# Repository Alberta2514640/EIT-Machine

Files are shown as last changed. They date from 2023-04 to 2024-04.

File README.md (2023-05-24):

# picoAWG
Arbitrary Waveform Generator for the Raspberry Pi Pico 16 Channels

## AWG Desktop Application
Desktop application to interface with Arbitrary Waveform Generator

TODO
- Implement Control of 16 Channels to Control Amplitude, Frequency, Offset 
- Read Back Output with Monitor to see the output
- Control LED s as needed

## PCB Design 
The board design for the waveform generator

TODO
- Update PCB design to include RP2040 directly and a cheaper OP AMP
- Update PCB design to shrink the design down to a more reasonable size and add a small status display beyond the current 5 status LEDs.

## RP2040 Code 
The code loaded onto the Pi Pico. 

TODO
- Monitor Output Needs to be fixed to setup the output
    - Write Values to the Output and Read Corresponding Voltage Changes 
- Control over channels 1-16 with Output Adjustments
    - Split the ADC control and the communication/ led control to seperate cores communicating between one another.
    - Utilize the PIO to drive the SPI peripheral and set the outputs appropriately. 
- Add functions to set the Configuration Register, Offset, Calibration, Data, Registers

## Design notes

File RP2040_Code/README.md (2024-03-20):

# RP2040 Embedded Code

This version of the RP2040 code runs on top of CircuitPython 9.0.0. It should work on earlier versions of CircuitPython as well, but they have not been tested.

CircuitPython can be downloaded [here](https://circuitpython.org/board/raspberry_pi_pico/) and the CircuitPython library bundle can be downloaded [here](https://circuitpython.org/libraries).

This project requires the `adafruit_pioasm.mpy`, `adafruit_74hc595.mpy` library files and the `adafruit_bus_directory` directory from the library bundle. Make sure you download the matching bundle for the version of CircuitPython you are using! Copy the listed items from the unzipped bundle into the `lib` directory on the RP2040's file system.

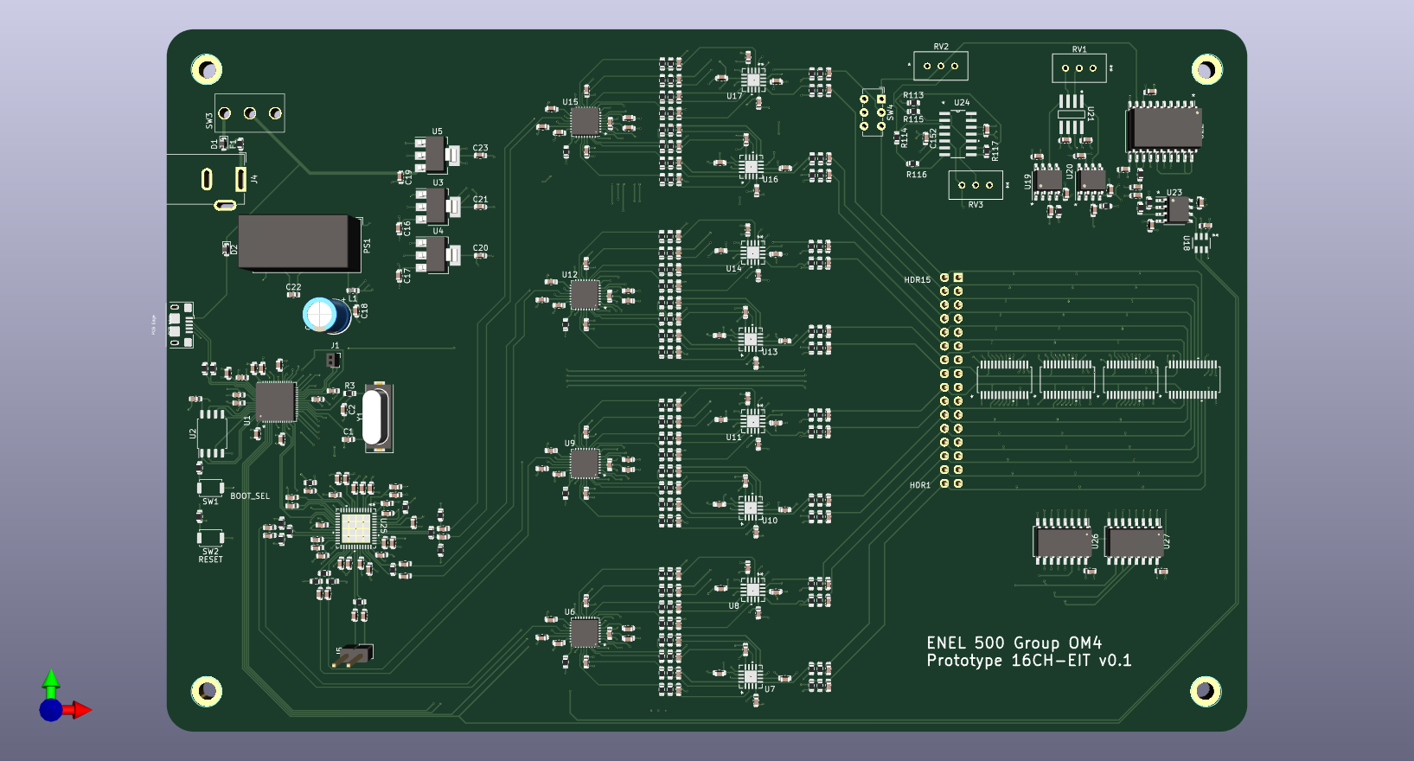
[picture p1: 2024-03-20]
PCB_Design/picoAWG_front.png

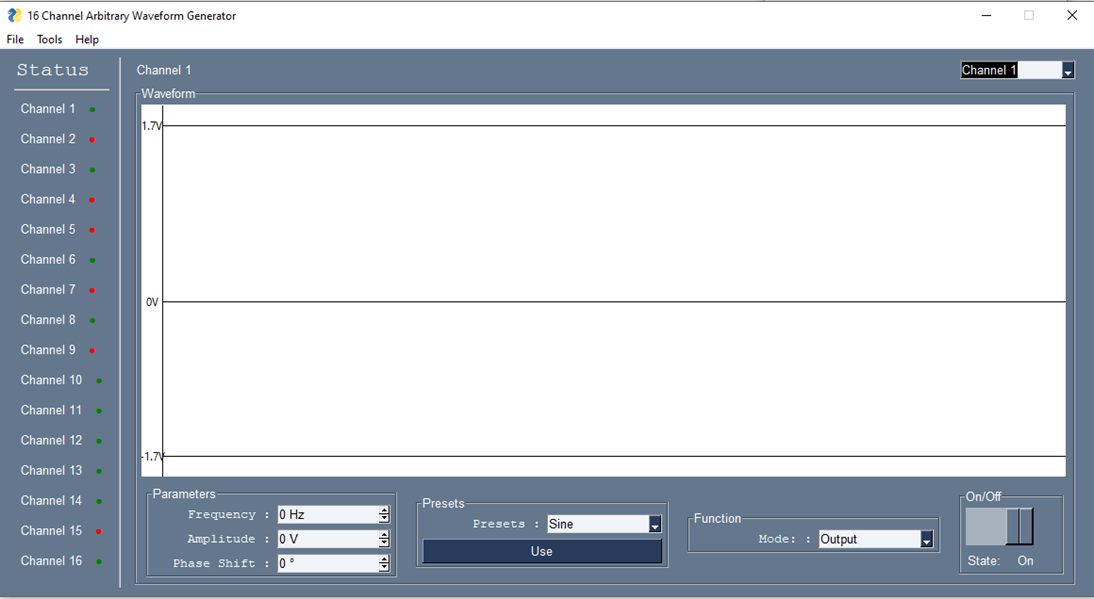
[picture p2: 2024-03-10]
AWG_DesktopApp/GUIDesign/Designed.png

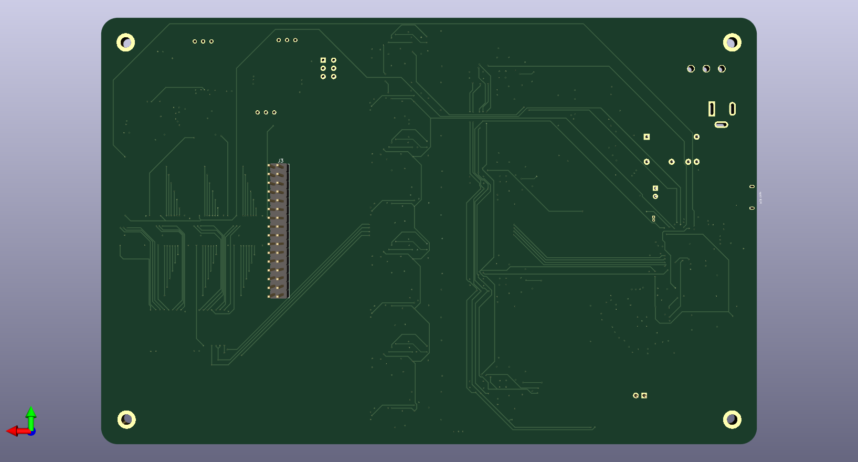
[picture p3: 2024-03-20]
PCB_Design/picoAWG_back.png

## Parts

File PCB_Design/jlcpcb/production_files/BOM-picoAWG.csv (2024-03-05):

Comment | Designator | Footprint | LCSC
SN74HC595 | U26,U27 | SOIC-16W_5.3x10.2mm_P1.27mm | C10092
27p | C1,C2 | C_0603_1608Metric | C107045
BOOT_SEL | SW1,SW2 | SW_Push_SPST_NO_Alps_SKRK | C115357
629105150521 | J2 | USB_Micro-B_Amphenol_10118193-0001LF_Horizontal | C132562
0.1u | C10,C100,C101,C102,C103,C108,C109,C11,C110,C115,C116,C117,C118,C119,C12,C124,C125,C126,C127,C128,C129,C13,C130,C131,C138,C139,C14,C140,C141,C142,C143,C144,C145,C146,C148,C149,C150,C151,C152,C153,C154,C155,C156,C157,C158,C159,C160,C161,C162,C163,C164,C165,C166,C167,C168,C169,C170,C171,C172,C173,C174,C175,C176,C177,C178,C179,C180,C181,C182,C183,C184,C185,C186,C187,C188,C189,C24,C25,C26,C3,C31,C32,C33,C34,C35,C40,C41,C42,C43,C44,C45,C46,C47,C5,C52,C53,C54,C59,C6,C60,C61,C62,C63,C68,C69,C70,C71,C72,C73,C74,C75,C8,C80,C81,C82,C87,C88,C89,C9,C90,C91,C96,C97,C98,C99 | C_0603_1608Metric | C14663
NCP1117-3.3_SOT223 | U3,U4 | SOT-223-3_TabPin2 | C146799
1u | C104,C105,C106,C107,C132,C133,C134,C135,C4,C48,C49,C50,C51,C7,C76,C77,C78,C79 | C_0603_1608Metric | C15849
1n | C136,C137 | C_0603_1608Metric | C1588
F0603E1R25FSTR | F1 | Fuse_0603_1608Metric | C163109
10p | C147 | C_0603_1608Metric | C1634
NCP1117-5.0_SOT223 | U5 | SOT-223-3_TabPin2 | C185806
10u | C16,C17,C19,C20,C21,C22,C23 | C_0603_1608Metric | C19702
RP2040 | U1 | QFN-56-1EP_7x7mm_P0.4mm_EP3.2x3.2mm | C2040
OPA4228UA | U24 | D14 | C2060814
1k | R100,R101,R113,R114,R115,R23,R24,R25,R26,R3,R4,R48,R49,R50,R51,R73,R74,R75,R76,R98,R99 | R_0603_1608Metric | C21190
470u | C15 | CP_Radial_D6.3mm_P2.50mm | C217537
100 | R123,R124,R125,R129,R131 | R_0603_1608Metric | C22775
1M | R106,R107,R109 | R_0603_1608Metric | C22935
499 | R10,R11,R116,R117,R12,R13,R14,R15,R16,R17,R18,R19,R20,R21,R31,R32,R33,R34,R35,R36,R37,R38,R39,R40,R41,R42,R43,R44,R45,R46,R56,R57,R58,R59,R6,R60,R61,R62,R63,R64,R65,R66,R67,R68,R69,R7,R70,R71,R8,R81,R82,R83,R84,R85,R86,R87,R88,R89,R9,R90,R91,R92,R93,R94,R95,R96 | R_0603_1608Metric | C23065
4.7k | R5 | R_0603_1608Metric | C23162
49.9 | R102,R103,R104,R105,R27,R28,R29,R30,R52,R53,R54,R55,R77,R78,R79,R80 | R_0603_1608Metric | C23185
240 | R119,R120,R121,R122,R126,R127 | R_0603_1608Metric | C23350
2.2u | C18 | C_0603_1608Metric | C23630
100k | R111 | R_0603_1608Metric | C25803
10k | R110 | R_0603_1608Metric | C25804
INA849DR | U21 | D0008A-IPC_A | C2871861
8.06K | R22,R47,R72,R97 | R_0603_1608Metric | C2984365
27.4 | R1,R2 | R_0603_1608Metric | C403125
1.5p | C111,C112,C113,C114,C120,C121,C122,C123,C27,C28,C29,C30,C36,C37,C38,C39,C55,C56,C57,C58,C64,C65,C66,C67,C83,C84,C85,C86,C92,C93,C94,C95 | C_0603_1608Metric | C5186670
TL071HD | U19,U20,U23 | SOIC-8_3.9x4.9mm_P1.27mm | C5214234
PMEG3020CEP | D1,D2 | D_0603_1608Metric | C552871
18u | L1 | L_0603_1608Metric | C57839
AD7680ARJZ-REEL7 | U18 | RJ_6_ADI | C578463
ADA4817-2ACPZ-R7 | U10,U11,U13,U14,U16,U17,U7,U8 | CP_16_4_ADI | C578929
ABLS-12.000MHZ-B4-T | Y1 | Crystal_SMD_HC49-SD | C596818
AD630ARZ | U22 | SOIC-20W_7.5x12.8mm_P1.27mm | C650378
AD9106BCP | U12,U15,U6,U9 | LFCSP-32-1EP_5x5mm_P0.5mm_EP3.6x3.6mm | C653186
AD9512BCPZ | U25 | CP_48_1_ADI | C653489
ADG1406BRUZ-REEL7 | U28,U29,U30,U31 | RU_28_ADI | C654796
4.12k | R128 | R_0603_1608Metric | C723644
50 | R130 | R_0603_1608Metric | C849792
W25Q128JVS | U2 | SOIC-8_5.23x5.23mm_P1.27mm | C97521

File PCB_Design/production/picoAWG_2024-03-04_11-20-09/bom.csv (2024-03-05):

Designator | Footprint | Quantity | Value | LCSC Part #
C1, C2 | 0603 | 2 | 27p
C10, C100, C101, C102, C103, C108, C109, C11, C110, C115, C116, C117, C118, C119, C12, C124, C125, C126, C127, C128, C129, C13, C130, C131, C138, C139, C14, C140, C141, C142, C143, C144, C145, C146, C148, C149, C150, C151, C152, C153, C154, C155, C156, C157, C158, C159, C160, C161, C162, C163, C164, C165, C166, C167, C168, C169, C170, C171, C172, C173, C174, C175, C176, C177, C178, C179, C180, C181, C182, C183, C184, C185, C186, C187, C188, C189, C24, C25, C26, C3, C31, C32, C33, C34, C35, C40, C41, C42, C43, C44, C45, C46, C47, C5, C52, C53, C54, C59, C6, C60, C61, C62, C63, C68, C69, C70, C71, C72, C73, C74, C75, C8, C80, C81, C82, C87, C88, C89, C9, C90, C91, C96, C97, C98, C99 | 0603 | 125 | 0.1u
C104, C105, C106, C107, C132, C133, C134, C135, C4, C48, C49, C50, C51, C7, C76, C77, C78, C79 | 0603 | 18 | 1u
C111, C112, C113, C114, C120, C121, C122, C123, C27, C28, C29, C30, C36, C37, C38, C39, C55, C56, C57, C58, C64, C65, C66, C67, C83, C84, C85, C86, C92, C93, C94, C95 | 0603 | 32 | 1.5p
C136, C137 | 0603 | 2 | 1n
C147 | 0603 | 1 | 10p
C15 | 0603 | 1 | 470u
C16, C17, C19, C20, C21, C22, C23 | 0603 | 7 | 10u
C18 | 0603 | 1 | 2.2u
D1, D2 | 0603 | 2 | PMEG3020CEP
F1 | 0603 | 1 | F0603E1R25FSTR
J1 | PinSocket_1x02_P1.00mm_Vertical | 1 | SWD_JP
J2 | USB_Micro-B_Wuerth_629105150521 | 1 | 629105150521
J3 | PinHeader_2x16_P2.54mm_Vertical | 1 | Conn_02x16
J4 | BarrelJack_GCT_DCJ200-10-A_Horizontal | 1 | Barrel_Jack
J5 | PinHeader_1x02_P2.54mm_Vertical | 1 | CLK4_DIAG
L1 | 0603 | 1 | 18u
PS1 | Converter_DCDC_XP_POWER-IAxxxxD_THT | 1 | IA0515D
R1, R2 | 0603 | 2 | 27.4
R10, R11, R12, R13, R14, R15, R16, R17, R18, R19, R20, R21, R31, R32, R33, R34, R35, R36, R37, R38, R39, R40, R41, R42, R43, R44, R45, R46, R56, R57, R58, R59, R6, R60, R61, R62, R63, R64, R65, R66, R67, R68, R69, R7, R70, R71, R8, R81, R82, R83, R84, R85, R86, R87, R88, R89, R9, R90, R91, R92, R93, R94, R95, R96 | 0603 | 64 | 499
R100, R101, R113, R114, R115, R23, R24, R25, R26, R3, R4, R48, R49, R50, R51, R73, R74, R75, R76, R98, R99 | 0603 | 21 | 1k
R102, R103, R104, R105, R27, R28, R29, R30, R52, R53, R54, R55, R77, R78, R79, R80 | 0603 | 16 | 49.9
R106, R107, R109 | 0603 | 3 | 1M
R110 | 0603 | 1 | 10k
R111 | 0603 | 1 | 100k
R116, R117 | 0603 | 2 | 500
R119, R120, R121, R122, R126, R127 | 0603 | 6 | 240
R123, R124, R125, R129, R131 | 0603 | 5 | 100
R128 | 0603 | 1 | 4.12k
R130 | 0603 | 1 | 50
R22, R47, R72, R97 | 0603 | 4 | 8.06K
R5 | 0603 | 1 | 4.7k
RV1, RV2 | POT_2023-08-01_VIS | 2 | M64W202KB40
RV3 | POT_2023-08-01_VIS | 1 | M64W103KB40
SW1 | SW_Push_SPST_NO_Alps_SKRK | 1 | BOOT_SEL
SW2 | SW_Push_SPST_NO_Alps_SKRK | 1 | SW_Push
SW3 | ANT11SF1CQE | 1 | ANT11SF1CQE
SW4 | SW_E-Switch_EG1271_SPDT | 1 | SW_SPDT_321
U1 | QFN-56-1EP_7x7mm_P0.4mm_EP3.2x3.2mm | 1 | RP2040
U10, U11, U13, U14, U16, U17, U7, U8 | CP_16_4_ADI | 8 | ADA4817-2ACPZ-R7
U12, U15, U6, U9 | LFCSP-32-1EP_5x5mm_P0.5mm_EP3.6x3.6mm | 4 | AD9106BCP
U18 | RJ_6_ADI | 1 | AD7680ARJZ-REEL7
U19, U20, U23 | TSSOP-8_3x3mm_P0.65mm | 3 | TL071
U2 | SOIC-8_5.23x5.23mm_P1.27mm | 1 | W25Q128JVS
U21 | D0008A-IPC_A | 1 | INA849DR
U22 | SOIC-20W_7.5x12.8mm_P1.27mm | 1 | AD630ARZ
U24 | D14 | 1 | OPA4228UA
U25 | CP_48_1_ADI | 1 | AD9512BCPZ
U26, U27 | SOIC-16W_5.3x10.2mm_P1.27mm | 2 | SN74HC595
U28, U29, U30, U31 | RU_28_ADI | 4 | ADG1406BRUZ-REEL7
U3, U4 | SOT-223-3_TabPin2 | 2 | NCP1117-3.3_SOT223
U5 | SOT-223-3_TabPin2 | 1 | NCP1117-5.0_SOT223
Y1 | Crystal_SMD_HC49-SD | 1 | ABLS-12.000MHZ-B4-T

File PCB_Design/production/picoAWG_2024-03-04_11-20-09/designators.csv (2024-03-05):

C1:1
C10:1
C100:1
C101:1
C102:1
C103:1
C104:1
C105:1
C106:1
C107:1
C108:1
C109:1
C11:1
C110:1
C111:1
C112:1
C113:1
C114:1
C115:1
C116:1
C117:1
C118:1
C119:1
C12:1
C120:1
C121:1
C122:1
C123:1
C124:1
C125:1
C126:1
C127:1
C128:1
C129:1
C13:1
C130:1
C131:1
C132:1
C133:1
C134:1
C135:1
C136:1
C137:1
C138:1
C139:1
C14:1
C140:1
C141:1
C142:1
C143:1
C144:1
C145:1
C146:1
C147:1
C148:1
C149:1
C15:1
C150:1
C151:1
C152:1
C153:1
C154:1
C155:1
C156:1
C157:1
C158:1
C159:1
C16:1
C160:1
C161:1
C162:1
C163:1
C164:1
C165:1
C166:1
C167:1
C168:1
C169:1
C17:1
C170:1
C171:1
C172:1
C173:1
C174:1
C175:1
C176:1
C177:1
C178:1
C179:1
C18:1
C180:1
C181:1
C182:1
C183:1
C184:1
C185:1
C186:1
C187:1
C188:1
C189:1
C19:1
C2:1
C20:1
C21:1
C22:1
C23:1
C24:1
C25:1
C26:1
C27:1
C28:1
C29:1
C3:1
C30:1
C31:1
C32:1
C33:1
C34:1
C35:1
C36:1
C37:1
C38:1
C39:1
C4:1
C40:1
C41:1
C42:1
C43:1
C44:1
C45:1
C46:1
C47:1
C48:1
C49:1
C5:1
C50:1
C51:1
C52:1
C53:1
C54:1
C55:1
C56:1
C57:1
C58:1
C59:1
C6:1
C60:1
C61:1
C62:1
C63:1
C64:1
C65:1
C66:1
C67:1
C68:1
C69:1
C7:1
C70:1
C71:1
C72:1
C73:1
C74:1
C75:1
C76:1
C77:1
C78:1
C79:1
C8:1
C80:1
C81:1
C82:1
C83:1
C84:1
C85:1
C86:1
C87:1
C88:1
C89:1
C9:1
C90:1
C91:1
C92:1
C93:1
C94:1
C95:1
C96:1
C97:1
C98:1
C99:1
D1:1
D2:1
F1:1
J1:1
J2:1
J3:1
J4:1
J5:1
L1:1
PS1:1
R1:1
R10:1
R100:1
R101:1
R102:1
R103:1
R104:1
R105:1
R106:1
R107:1
R109:1
R11:1
R110:1
R111:1
R113:1
R114:1
R115:1
R116:1
R117:1
R119:1
R12:1
R120:1
R121:1
R122:1
R123:1
R124:1
R125:1
R126:1
R127:1
R128:1
R129:1
R13:1
R130:1
R131:1
R14:1
R15:1
R16:1
R17:1
R18:1
R19:1
R2:1
R20:1
R21:1
R22:1
R23:1
R24:1
R25:1
R26:1
R27:1
R28:1
R29:1
R3:1
R30:1
R31:1
R32:1
R33:1
R34:1
R35:1
R36:1
R37:1
R38:1
R39:1
R4:1
R40:1
R41:1
R42:1
R43:1
R44:1
R45:1
R46:1
R47:1
R48:1
R49:1
R5:1
R50:1
R51:1
R52:1
R53:1
R54:1
R55:1
R56:1
R57:1
R58:1
R59:1
R6:1
R60:1
R61:1
R62:1
R63:1
R64:1
R65:1
R66:1
R67:1
R68:1
R69:1
R7:1
R70:1
R71:1
R72:1
R73:1
R74:1
R75:1
R76:1
R77:1
R78:1
R79:1
R8:1
R80:1
R81:1
R82:1
R83:1
R84:1
R85:1
R86:1
R87:1
R88:1
R89:1
R9:1
R90:1
R91:1
R92:1
R93:1
R94:1
R95:1
R96:1
R97:1
R98:1
R99:1
REF**:4
RV1:1
RV2:1
RV3:1
SW1:1
SW2:1
SW3:1
SW4:1
U1:1
U10:1
U11:1
U12:1
U13:1
U14:1
U15:1
U16:1
U17:1
U18:1
U19:1
U2:1
U20:1
U21:1
U22:1
U23:1
U24:1
U25:1
U26:1
U27:1
U28:1
U29:1
U3:1
U30:1
U31:1
U4:1
U5:1
U6:1
U7:1
U8:1
U9:1
Y1:1

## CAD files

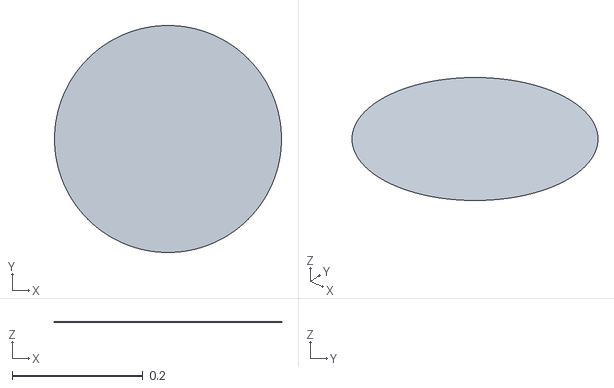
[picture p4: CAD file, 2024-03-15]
AWG_DesktopApp/EIT/JAC/Meshes/Circle.ply
0.348 x 0.348 x 3.04e-08

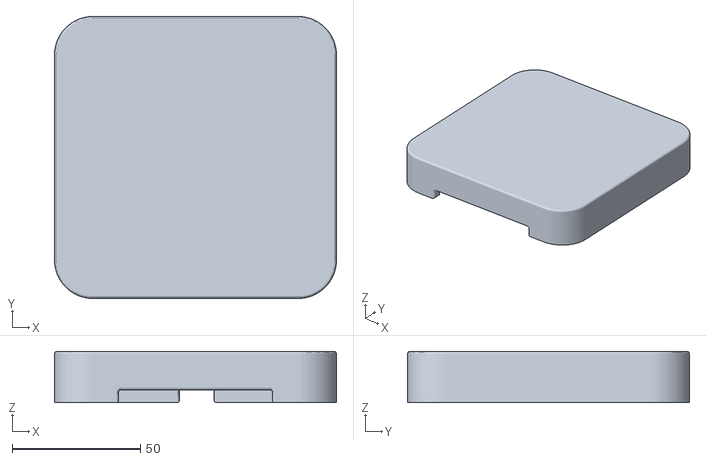
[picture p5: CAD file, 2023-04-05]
Enclosure/AWG v1_Top.stl
110.0 x 110.0 x 20.0

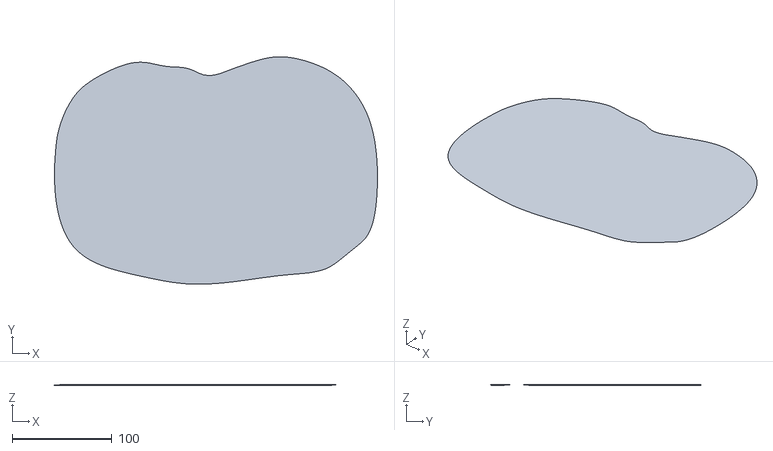
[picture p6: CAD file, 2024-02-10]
AWG_DesktopApp/EIT/JAC/Meshes/mesha06_bumpychestslice_radiological_view_both_lungs_1_0-3.ply
324.5 x 228.5 x 2e-05

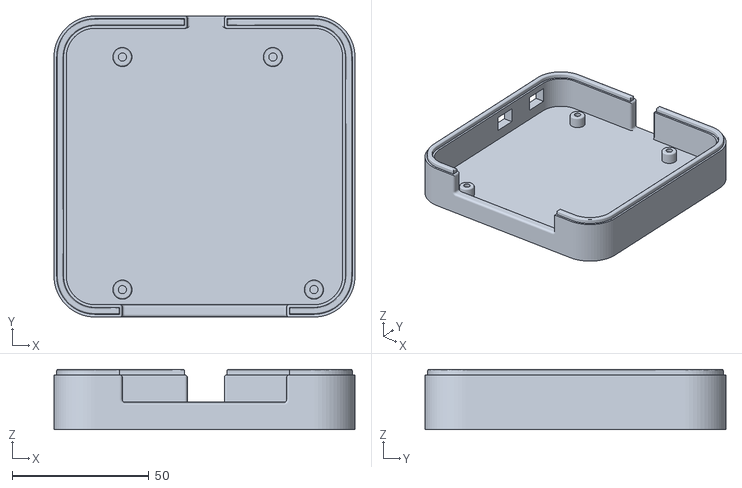
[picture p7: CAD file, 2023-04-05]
Enclosure/AWG v1_Bottom.stl
110.0 x 110.0 x 22.0

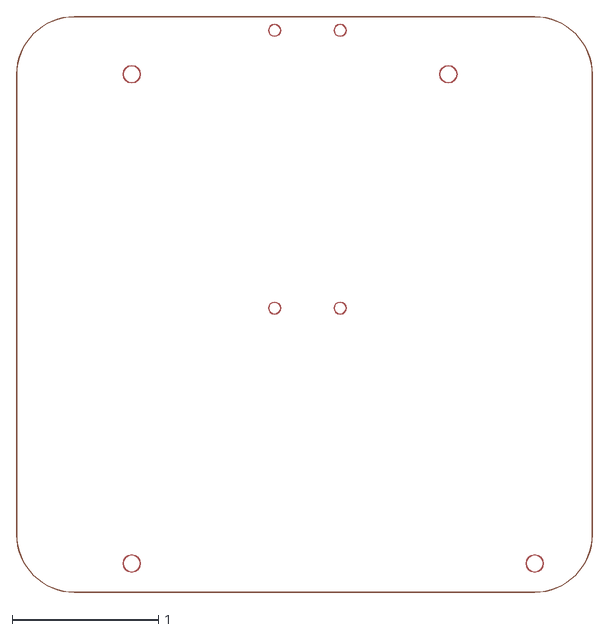
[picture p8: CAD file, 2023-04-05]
Enclosure/BoardOutline.dxf
3.94 x 3.94

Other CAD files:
Enclosure/AWG v1.f3d

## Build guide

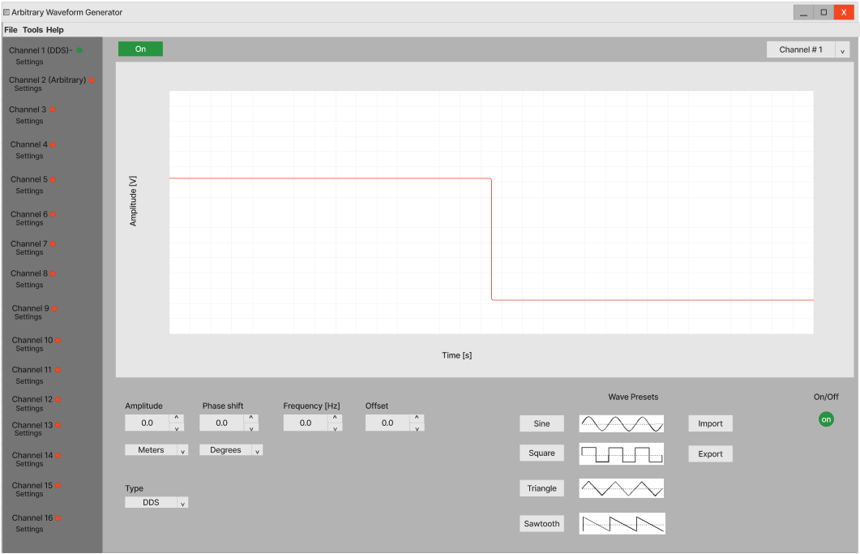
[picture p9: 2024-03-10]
AWG_DesktopApp/GUIDesign/Figma.png

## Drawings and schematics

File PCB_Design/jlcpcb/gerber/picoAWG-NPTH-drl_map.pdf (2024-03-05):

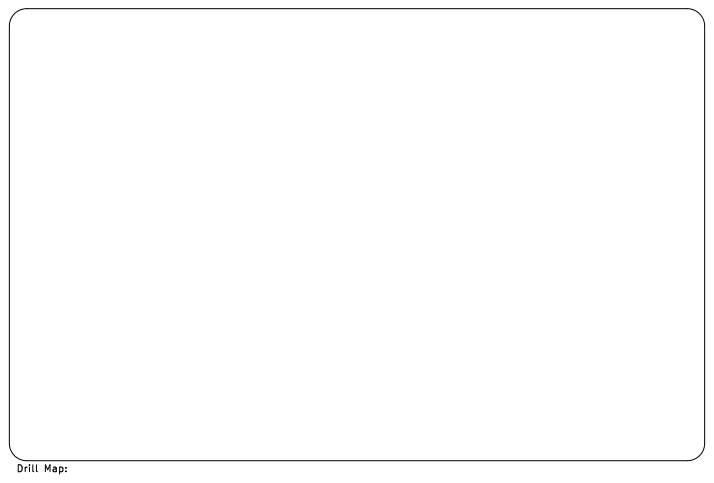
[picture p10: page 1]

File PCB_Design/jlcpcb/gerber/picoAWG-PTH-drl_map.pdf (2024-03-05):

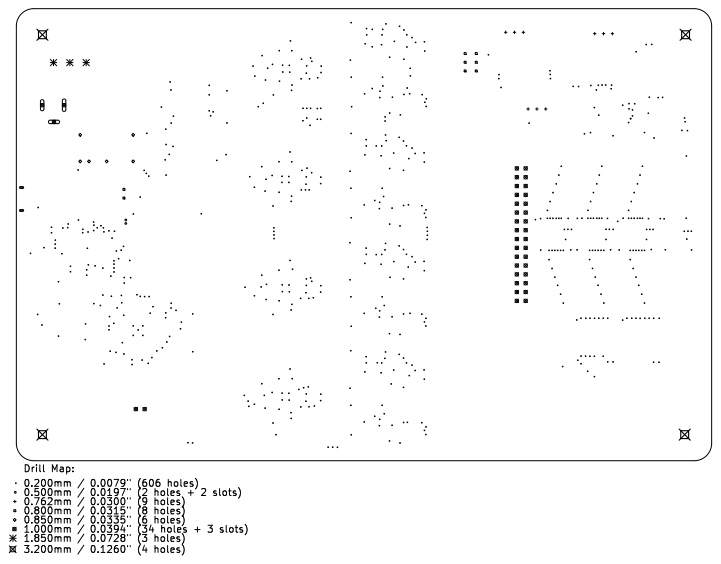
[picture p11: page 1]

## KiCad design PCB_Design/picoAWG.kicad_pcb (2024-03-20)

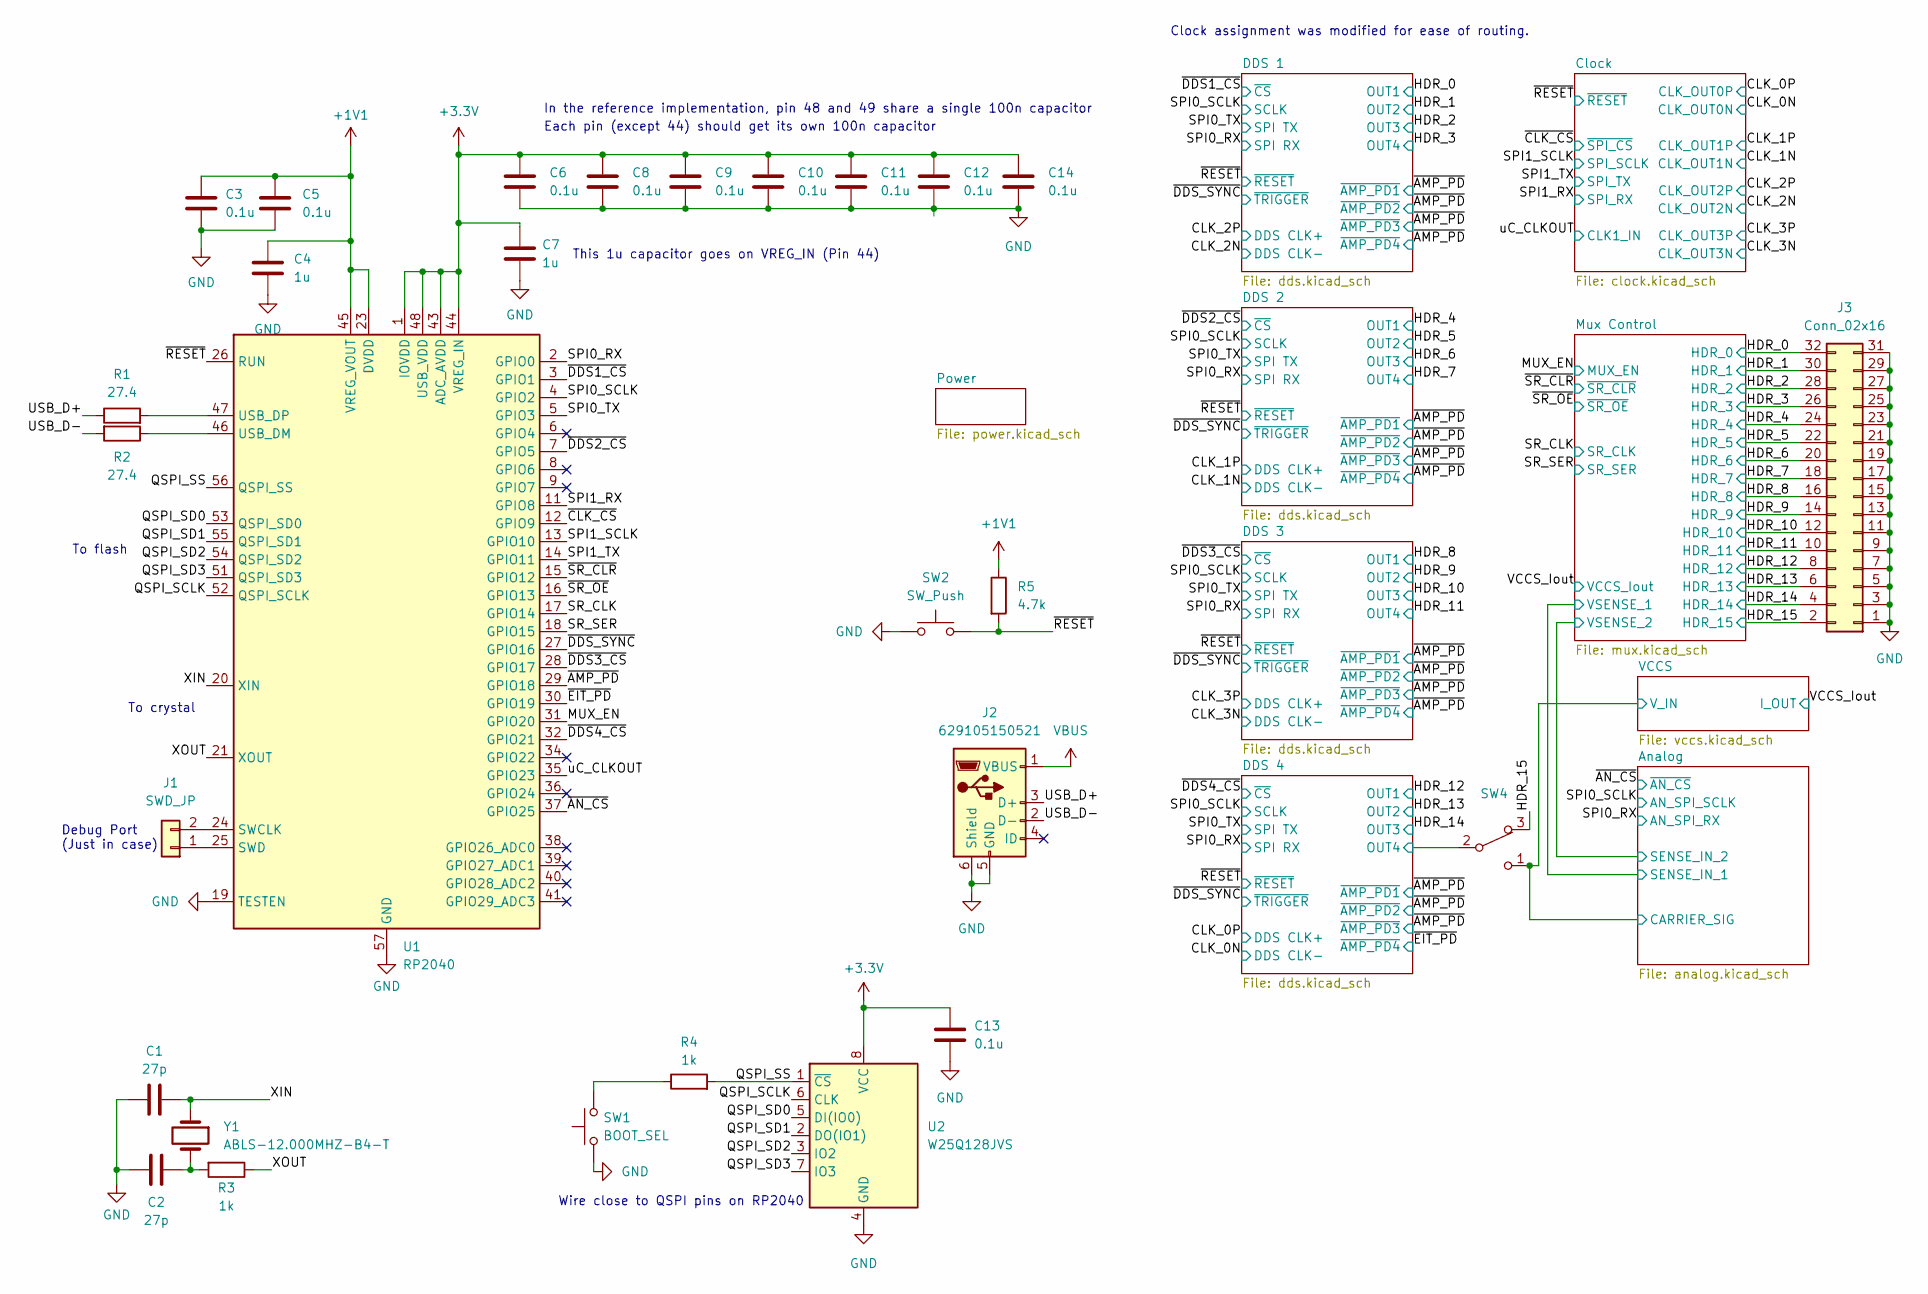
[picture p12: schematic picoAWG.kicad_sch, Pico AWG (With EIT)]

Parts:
C1, C2: 27p; C_0603_1608Metric
C3, C5, C6, C8, C9, C10, C11, C12, C13, C14: 0.1u; C_0603_1608Metric
C4, C7: 1u; C_0603_1608Metric
J1: SWD_JP; PinSocket_1x02_P1.00mm_Vertical
J2: 629105150521; USB_Micro-B_Amphenol_10118193-0001LF_Horizontal
J3: Conn_02x16; PinHeader_2x16_P2.54mm_Vertical
R1, R2: 27.4; R_0603_1608Metric
R3, R4: 1k; R_0603_1608Metric
R5: 4.7k; R_0603_1608Metric
SW1: BOOT_SEL; SW_Push_SPST_NO_Alps_SKRK
SW2: SW_Push; SW_Push_SPST_NO_Alps_SKRK
SW4: SW_SPDT_321; SW_E-Switch_EG1271_SPDT
U1: RP2040; QFN-56-1EP_7x7mm_P0.4mm_EP3.2x3.2mm
U2: W25Q128JVS; SOIC-8_5.23x5.23mm_P1.27mm
Y1: ABLS-12.000MHZ-B4-T; Crystal_SMD_HC49-SD

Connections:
+1V1: C3.1, C4.1, C5.1, R5.1, U1.23 (DVDD), U1.45 (VREG_VOUT), U1.50 (DVDD)
+3.3V: C6.1, C7.1, C8.1, C9.1, C10.1, C11.1, C12.1, C13.1, C14.1, U1.1 (IOVDD), U1.10 (IOVDD), U1.22 (IOVDD), U1.33 (IOVDD), U1.42 (IOVDD), U1.43 (ADC_AVDD), U1.44 (VREG_IN), U1.48 (USB_VDD), U1.49 (IOVDD), U2.8 (VCC); also elsewhere on the board
/Analog/CARRIER_SIG: SW4.1 (C); also elsewhere on the board
/DDS 4/OUT4: SW4.2 (B); also elsewhere on the board
/HDR_0: J3.32; also elsewhere on the board
/HDR_1: J3.30; also elsewhere on the board
/HDR_2: J3.28; also elsewhere on the board
/HDR_3: J3.26; also elsewhere on the board
/HDR_4: J3.24; also elsewhere on the board
/HDR_5: J3.22; also elsewhere on the board
/HDR_6: J3.20; also elsewhere on the board
/HDR_7: J3.18; also elsewhere on the board
/HDR_8: J3.16; also elsewhere on the board
/HDR_9: J3.14; also elsewhere on the board
/HDR_10: J3.12; also elsewhere on the board
/HDR_11: J3.10; also elsewhere on the board
/HDR_12: J3.8; also elsewhere on the board
/HDR_13: J3.6; also elsewhere on the board
/HDR_14: J3.4; also elsewhere on the board
/HDR_15: J3.2, SW4.3 (A); also elsewhere on the board
/MUX_EN: U1.31 (GPIO20); also elsewhere on the board
/QSPI_SCLK: U1.52 (QSPI_SCLK), U2.6 (CLK)
/QSPI_SD0: U1.53 (QSPI_SD0), U2.5 (DI(IO0))
/QSPI_SD1: U1.55 (QSPI_SD1), U2.2 (DO(IO1))
/QSPI_SD2: U1.54 (QSPI_SD2), U2.3 (IO2)
/QSPI_SD3: U1.51 (QSPI_SD3), U2.7 (IO3)
/QSPI_SS: R4.2, U1.56 (QSPI_SS), U2.1 (~CS)
/SPI0_RX: U1.2 (GPIO0); also elsewhere on the board
/SPI0_SCLK: U1.4 (GPIO2); also elsewhere on the board
/SPI0_TX: U1.5 (GPIO3); also elsewhere on the board
/SPI1_RX: U1.11 (GPIO8); also elsewhere on the board
/SPI1_SCLK: U1.13 (GPIO10); also elsewhere on the board
/SPI1_TX: U1.14 (GPIO11); also elsewhere on the board
/SR_CLK: U1.17 (GPIO14); also elsewhere on the board
/SR_SER: U1.18 (GPIO15); also elsewhere on the board
/USB_D+: J2.3 (D+), R1.1
/USB_D-: J2.2 (D-), R2.2
/XIN: C1.2, U1.20 (XIN), Y1.1
/XOUT: R3.1, U1.21 (XOUT)
/uC_CLKOUT: U1.35 (GPIO23); also elsewhere on the board
/~AMP_PD: U1.29 (GPIO18); also elsewhere on the board
/~AN_CS: U1.37 (GPIO25); also elsewhere on the board
/~CLK_CS: U1.12 (GPIO9); also elsewhere on the board
/~DDS1_CS: U1.3 (GPIO1); also elsewhere on the board
/~DDS2_CS: U1.7 (GPIO5); also elsewhere on the board
/~DDS3_CS: U1.28 (GPIO17); also elsewhere on the board
/~DDS4_CS: U1.32 (GPIO21); also elsewhere on the board
/~DDS_SYNC: U1.27 (GPIO16); also elsewhere on the board
/~EIT_PD: U1.30 (GPIO19); also elsewhere on the board
/~RESET: R5.2, SW2.2, U1.26 (RUN); also elsewhere on the board
/~SR_CLR: U1.15 (GPIO12); also elsewhere on the board
/~SR_OE: U1.16 (GPIO13); also elsewhere on the board
GND: C1.1, C2.2, C3.2, C4.2, C5.2, C6.2, C7.2, C8.2, C9.2, C10.2, C11.2, C12.2, C13.2, C14.2, J2.5 (GND), J2.6 (Shield), J3.1, J3.3, J3.5, J3.7, J3.9, J3.11, J3.13, J3.15, J3.17, J3.19, J3.21, J3.23, J3.25, J3.27, J3.29, J3.31, SW1.1, SW2.1, U1.19 (TESTEN), U1.57 (GND), U2.4 (GND); also elsewhere on the board
unnamed: C2.1, R3.2, Y1.2
unnamed: J1.1, U1.25 (SWD)
unnamed: J1.2, U1.24 (SWCLK)
unnamed: R4.1, SW1.2
unnamed: R2.1, U1.46 (USB_DM)
unnamed: R1.2, U1.47 (USB_DP)
VBUS: J2.1 (VBUS); also elsewhere on the board

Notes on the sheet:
Each pin (except 44) should get its own 100n capacitor
To crystal
Debug Port (Just in case)
This 1u capacitor goes on VREG_IN (Pin 44)
To flash
Clock assignment was modified for ease of routing.
In the reference implementation, pin 48 and 49 share a single 100n capacitor
Wire close to QSPI pins on RP2040

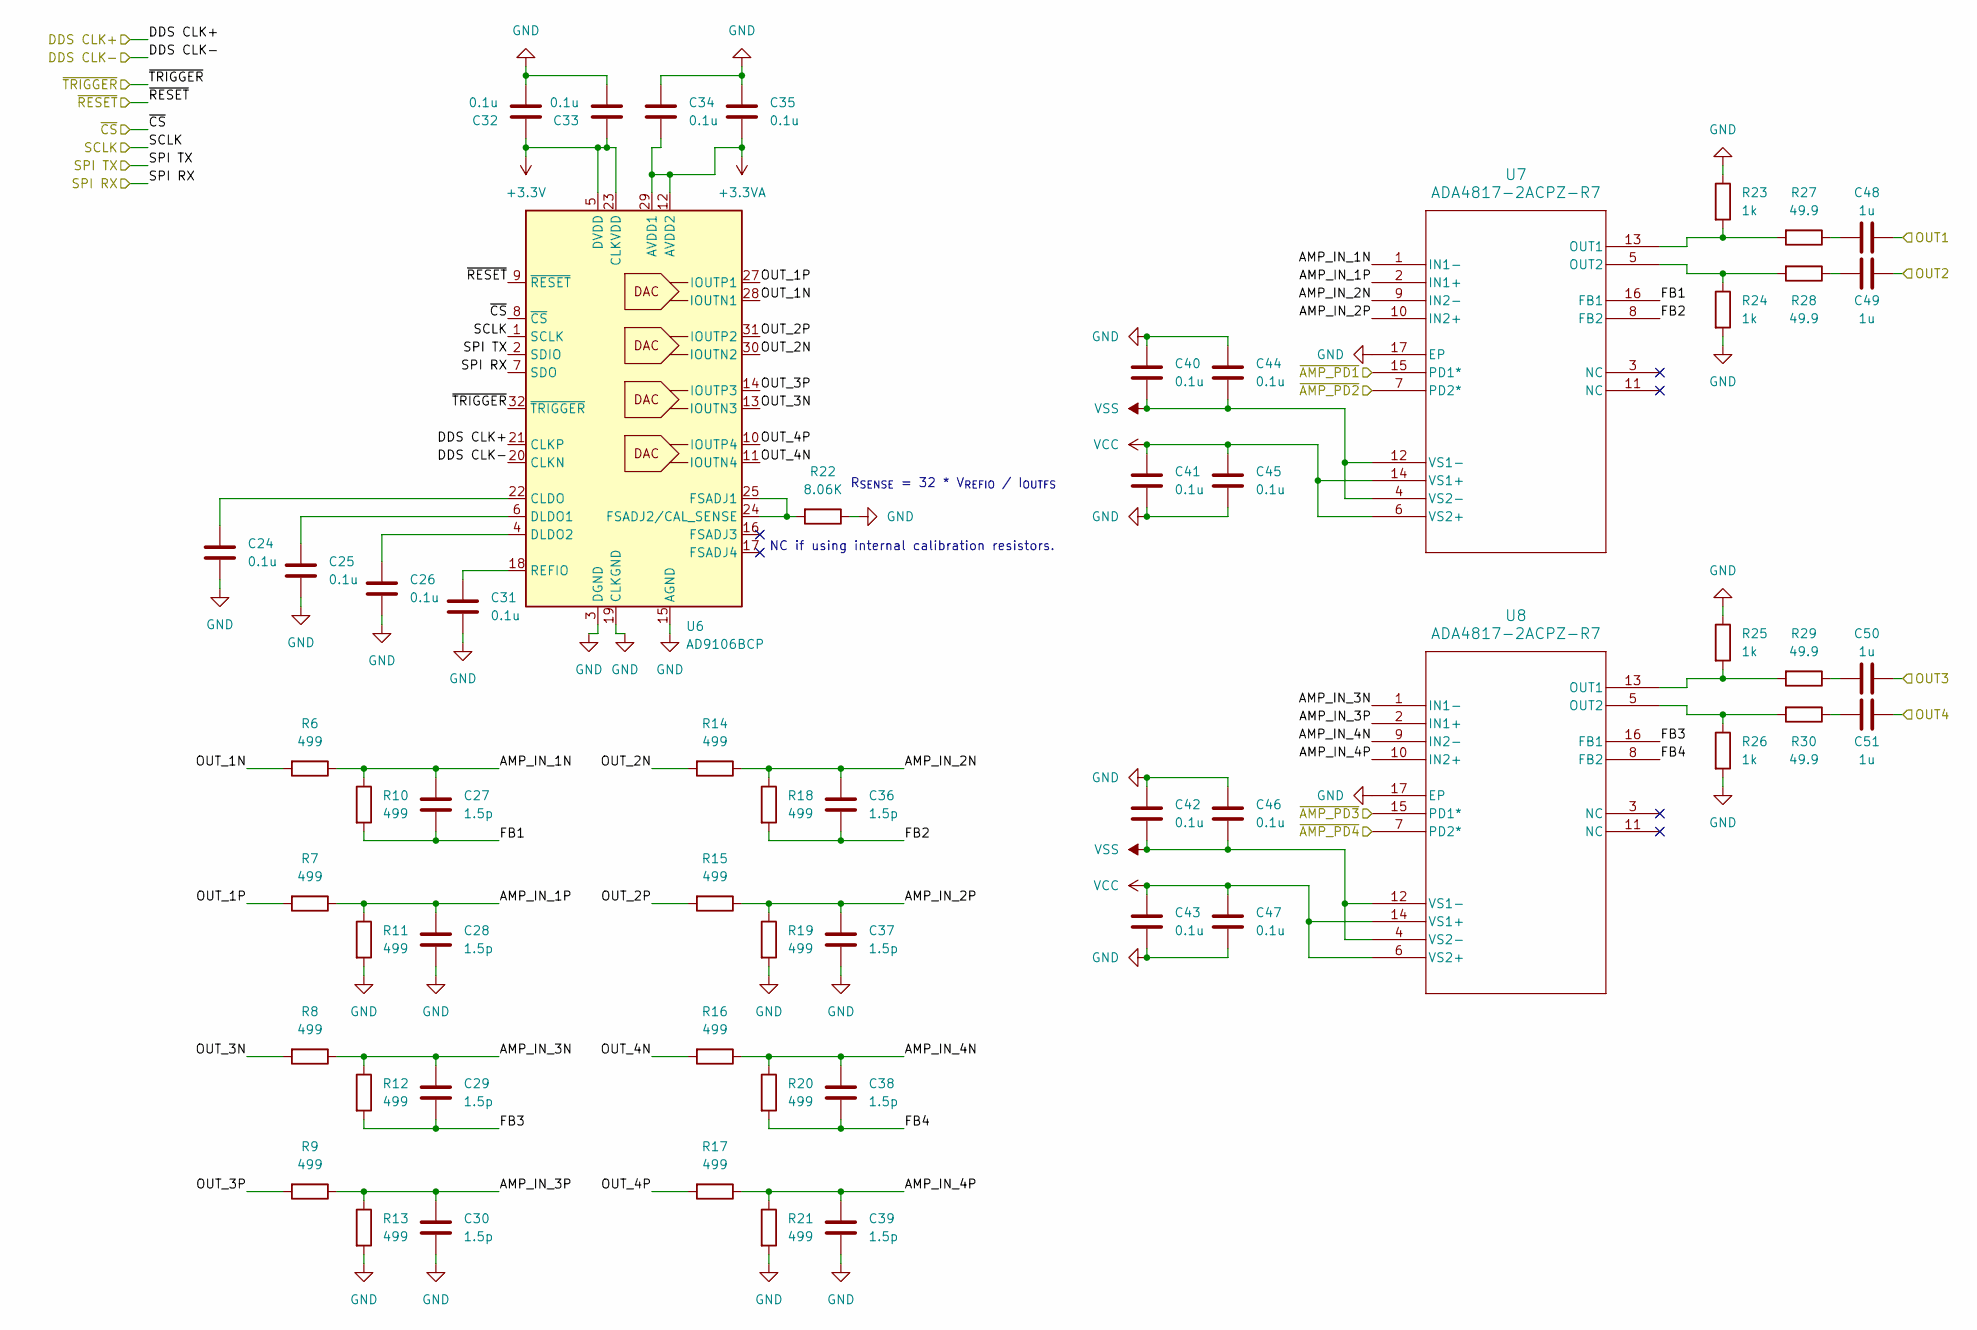
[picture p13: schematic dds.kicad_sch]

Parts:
C24, C25, C26, C31, C32, C33, C34, C35, C40, C41, C42, C43, C44, C45, C46, C47: 0.1u; C_0603_1608Metric
C27, C28, C29, C30, C36, C37, C38, C39: 1.5p; C_0603_1608Metric
C48, C49, C50, C51: 1u; C_0603_1608Metric
R6, R7, R8, R9, R10, R11, R12, R13, R14, R15, R16, R17, R18, R19, R20, R21: 499; R_0603_1608Metric
R22: 8.06K; R_0603_1608Metric
R23, R24, R25, R26: 1k; R_0603_1608Metric
R27, R28, R29, R30: 49.9; R_0603_1608Metric
U6: AD9106BCP; LFCSP-32-1EP_5x5mm_P0.5mm_EP3.6x3.6mm
U7, U8: ADA4817-2ACPZ-R7; CP_16_4_ADI

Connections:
+3.3V: C32.1, C33.1, U6.5 (DVDD), U6.23 (CLKVDD); also elsewhere on the board
+3.3VA: C34.2, C35.2, U6.12 (AVDD2), U6.29 (AVDD1); also elsewhere on the board
/CLK_2N: U6.20 (CLKN); also elsewhere on the board
/CLK_2P: U6.21 (CLKP); also elsewhere on the board
/DDS 1/AMP_IN_1N: C27.1, R6.1, R10.1, U7.1 (IN1-)
/DDS 1/AMP_IN_1P: C28.1, R7.1, R11.1, U7.2 (IN1+)
/DDS 1/AMP_IN_2N: C36.1, R14.1, R18.1, U7.9 (IN2-)
/DDS 1/AMP_IN_2P: C37.1, R15.1, R19.1, U7.10 (IN2+)
/DDS 1/AMP_IN_3N: C29.1, R8.1, R12.1, U8.1 (IN1-)
/DDS 1/AMP_IN_3P: C30.1, R9.1, R13.1, U8.2 (IN1+)
/DDS 1/AMP_IN_4N: C38.1, R16.1, R20.1, U8.9 (IN2-)
/DDS 1/AMP_IN_4P: C39.1, R17.1, R21.1, U8.10 (IN2+)
/DDS 1/FB1: C27.2, R10.2, U7.16 (FB1)
/DDS 1/FB2: C36.2, R18.2, U7.8 (FB2)
/DDS 1/FB3: C29.2, R12.2, U8.16 (FB1)
/DDS 1/FB4: C38.2, R20.2, U8.8 (FB2)
/DDS 1/OUT_1N: R6.2, U6.28 (IOUTN1)
/DDS 1/OUT_1P: R7.2, U6.27 (IOUTP1)
/DDS 1/OUT_2N: R14.2, U6.30 (IOUTN2)
/DDS 1/OUT_2P: R15.2, U6.31 (IOUTP2)
/DDS 1/OUT_3N: R8.2, U6.13 (IOUTN3)
/DDS 1/OUT_3P: R9.2, U6.14 (IOUTP3)
/DDS 1/OUT_4N: R16.2, U6.11 (IOUTN4)
/DDS 1/OUT_4P: R17.2, U6.10 (IOUTP4)
/HDR_0: C48.2; also elsewhere on the board
/HDR_1: C49.2; also elsewhere on the board
/HDR_2: C50.2; also elsewhere on the board
/HDR_3: C51.2; also elsewhere on the board
/SPI0_RX: U6.7 (SDO); also elsewhere on the board
/SPI0_SCLK: U6.1 (SCLK); also elsewhere on the board
/SPI0_TX: U6.2 (SDIO); also elsewhere on the board
/~AMP_PD: U7.7 (PD2*), U7.15 (PD1*), U8.7 (PD2*), U8.15 (PD1*); also elsewhere on the board
/~DDS1_CS: U6.8 (~CS); also elsewhere on the board
/~DDS_SYNC: U6.32 (~TRIGGER); also elsewhere on the board
/~RESET: U6.9 (~RESET); also elsewhere on the board
GND: C24.1, C25.1, C26.1, C28.2, C30.2, C31.1, C32.2, C33.2, C34.1, C35.1, C37.2, C39.2, C40.1, C41.2, C42.1, C43.2, C44.1, C45.2, C46.1, C47.2, R11.2, R13.2, R19.2, R21.2, R22.1, R23.1, R24.2, R25.1, R26.2, U6.3 (DGND), U6.15 (AGND), U6.19 (CLKGND), U6.26 (AGND), U6.33 (DGND), U7.17 (EP), U8.17 (EP); also elsewhere on the board
unnamed: C48.1, R27.1
unnamed: C49.1, R28.1
unnamed: C50.1, R29.1
unnamed: C51.1, R30.1
unnamed: C24.2, U6.22 (CLDO)
unnamed: C25.2, U6.6 (DLDO1)
unnamed: C26.2, U6.4 (DLDO2)
unnamed: R22.2, U6.24 (FSADJ2/CAL_SENSE), U6.25 (FSADJ1)
unnamed: C31.2, U6.18 (REFIO)
unnamed: R23.2, R27.2, U7.13 (OUT1)
unnamed: R24.1, R28.2, U7.5 (OUT2)
unnamed: R25.2, R29.2, U8.13 (OUT1)
unnamed: R26.1, R30.2, U8.5 (OUT2)
VCC: C41.1, C43.1, C45.1, C47.1, U7.6 (VS2+), U7.14 (VS1+), U8.6 (VS2+), U8.14 (VS1+); also elsewhere on the board
VSS: C40.2, C42.2, C44.2, C46.2, U7.4 (VS2-), U7.12 (VS1-), U8.4 (VS2-), U8.12 (VS1-); also elsewhere on the board

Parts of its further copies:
C52, C53, C54, C59, C60, C61, C62, C63, C68, C69, C70, C71, C72, C73, C74, C75, C80, C81, C82, C87, C88, C89, C90, C91, C96, C97, C98, C99, C100, C101, C102, C103, C108, C109, C110, C115, C116, C117, C118, C119, C124, C125, C126, C127, C128, C129, C130, C131: 0.1u; C_0603_1608Metric
C55, C56, C57, C58, C64, C65, C66, C67, C83, C84, C85, C86, C92, C93, C94, C95, C111, C112, C113, C114, C120, C121, C122, C123: 1.5p; C_0603_1608Metric
C76, C77, C78, C79, C104, C105, C106, C107, C132, C133, C134, C135: 1u; C_0603_1608Metric
R31, R32, R33, R34, R35, R36, R37, R38, R39, R40, R41, R42, R43, R44, R45, R46, R56, R57, R58, R59, R60, R61, R62, R63, R64, R65, R66, R67, R68, R69, R70, R71, R81, R82, R83, R84, R85, R86, R87, R88, R89, R90, R91, R92, R93, R94, R95, R96: 499; R_0603_1608Metric
R47, R72, R97: 8.06K; R_0603_1608Metric
R48, R49, R50, R51, R73, R74, R75, R76, R98, R99, R100, R101: 1k; R_0603_1608Metric
R52, R53, R54, R55, R77, R78, R79, R80, R102, R103, R104, R105: 49.9; R_0603_1608Metric
U9, U12, U15: AD9106BCP; LFCSP-32-1EP_5x5mm_P0.5mm_EP3.6x3.6mm
U10, U11, U13, U14, U16, U17: ADA4817-2ACPZ-R7; CP_16_4_ADI

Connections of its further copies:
+3.3V: C60.1, C61.1, C88.1, C89.1, C116.1, C117.1, U9.5 (DVDD), U9.23 (CLKVDD), U12.5 (DVDD), U12.23 (CLKVDD), U15.5 (DVDD), U15.23 (CLKVDD); also elsewhere on the board
+3.3VA: C62.2, C63.2, C90.2, C91.2, C118.2, C119.2, U9.12 (AVDD2), U9.29 (AVDD1), U12.12 (AVDD2), U12.29 (AVDD1), U15.12 (AVDD2), U15.29 (AVDD1); also elsewhere on the board
/CLK_0N: U15.20 (CLKN); also elsewhere on the board
/CLK_0P: U15.21 (CLKP); also elsewhere on the board
/CLK_1N: U9.20 (CLKN); also elsewhere on the board
/CLK_1P: U9.21 (CLKP); also elsewhere on the board
/CLK_3N: U12.20 (CLKN); also elsewhere on the board
/CLK_3P: U12.21 (CLKP); also elsewhere on the board
/DDS 2/AMP_IN_1N: C55.1, R31.1, R35.1, U10.1 (IN1-)
/DDS 2/AMP_IN_1P: C56.1, R32.1, R36.1, U10.2 (IN1+)
/DDS 2/AMP_IN_2N: C64.1, R39.1, R43.1, U10.9 (IN2-)
/DDS 2/AMP_IN_2P: C65.1, R40.1, R44.1, U10.10 (IN2+)
/DDS 2/AMP_IN_3N: C57.1, R33.1, R37.1, U11.1 (IN1-)
/DDS 2/AMP_IN_3P: C58.1, R34.1, R38.1, U11.2 (IN1+)
/DDS 2/AMP_IN_4N: C66.1, R41.1, R45.1, U11.9 (IN2-)
/DDS 2/AMP_IN_4P: C67.1, R42.1, R46.1, U11.10 (IN2+)
/DDS 2/FB1: C55.2, R35.2, U10.16 (FB1)
/DDS 2/FB2: C64.2, R43.2, U10.8 (FB2)
/DDS 2/FB3: C57.2, R37.2, U11.16 (FB1)
/DDS 2/FB4: C66.2, R45.2, U11.8 (FB2)
/DDS 2/OUT_1N: R31.2, U9.28 (IOUTN1)
/DDS 2/OUT_1P: R32.2, U9.27 (IOUTP1)
/DDS 2/OUT_2N: R39.2, U9.30 (IOUTN2)
/DDS 2/OUT_2P: R40.2, U9.31 (IOUTP2)
/DDS 2/OUT_3N: R33.2, U9.13 (IOUTN3)
/DDS 2/OUT_3P: R34.2, U9.14 (IOUTP3)
/DDS 2/OUT_4N: R41.2, U9.11 (IOUTN4)
/DDS 2/OUT_4P: R42.2, U9.10 (IOUTP4)
/DDS 3/AMP_IN_1N: C83.1, R56.1, R60.1, U13.1 (IN1-)
/DDS 3/AMP_IN_1P: C84.1, R57.1, R61.1, U13.2 (IN1+)
/DDS 3/AMP_IN_2N: C92.1, R64.1, R68.1, U13.9 (IN2-)
/DDS 3/AMP_IN_2P: C93.1, R65.1, R69.1, U13.10 (IN2+)
/DDS 3/AMP_IN_3N: C85.1, R58.1, R62.1, U14.1 (IN1-)
/DDS 3/AMP_IN_3P: C86.1, R59.1, R63.1, U14.2 (IN1+)
/DDS 3/AMP_IN_4N: C94.1, R66.1, R70.1, U14.9 (IN2-)
/DDS 3/AMP_IN_4P: C95.1, R67.1, R71.1, U14.10 (IN2+)
/DDS 3/FB1: C83.2, R60.2, U13.16 (FB1)
/DDS 3/FB2: C92.2, R68.2, U13.8 (FB2)
/DDS 3/FB3: C85.2, R62.2, U14.16 (FB1)
/DDS 3/FB4: C94.2, R70.2, U14.8 (FB2)
/DDS 3/OUT_1N: R56.2, U12.28 (IOUTN1)
/DDS 3/OUT_1P: R57.2, U12.27 (IOUTP1)
/DDS 3/OUT_2N: R64.2, U12.30 (IOUTN2)
/DDS 3/OUT_2P: R65.2, U12.31 (IOUTP2)
/DDS 3/OUT_3N: R58.2, U12.13 (IOUTN3)
/DDS 3/OUT_3P: R59.2, U12.14 (IOUTP3)
/DDS 3/OUT_4N: R66.2, U12.11 (IOUTN4)
/DDS 3/OUT_4P: R67.2, U12.10 (IOUTP4)
/DDS 4/AMP_IN_1N: C111.1, R81.1, R85.1, U16.1 (IN1-)
/DDS 4/AMP_IN_1P: C112.1, R82.1, R86.1, U16.2 (IN1+)
/DDS 4/AMP_IN_2N: C120.1, R89.1, R93.1, U16.9 (IN2-)
/DDS 4/AMP_IN_2P: C121.1, R90.1, R94.1, U16.10 (IN2+)
/DDS 4/AMP_IN_3N: C113.1, R83.1, R87.1, U17.1 (IN1-)
/DDS 4/AMP_IN_3P: C114.1, R84.1, R88.1, U17.2 (IN1+)
/DDS 4/AMP_IN_4N: C122.1, R91.1, R95.1, U17.9 (IN2-)
/DDS 4/AMP_IN_4P: C123.1, R92.1, R96.1, U17.10 (IN2+)
/DDS 4/FB1: C111.2, R85.2, U16.16 (FB1)
/DDS 4/FB2: C120.2, R93.2, U16.8 (FB2)
/DDS 4/FB3: C113.2, R87.2, U17.16 (FB1)
/DDS 4/FB4: C122.2, R95.2, U17.8 (FB2)
/DDS 4/OUT4: C135.2; also elsewhere on the board
/DDS 4/OUT_1N: R81.2, U15.28 (IOUTN1)
/DDS 4/OUT_1P: R82.2, U15.27 (IOUTP1)
/DDS 4/OUT_2N: R89.2, U15.30 (IOUTN2)
/DDS 4/OUT_2P: R90.2, U15.31 (IOUTP2)
/DDS 4/OUT_3N: R83.2, U15.13 (IOUTN3)
/DDS 4/OUT_3P: R84.2, U15.14 (IOUTP3)
/DDS 4/OUT_4N: R91.2, U15.11 (IOUTN4)
/DDS 4/OUT_4P: R92.2, U15.10 (IOUTP4)
/HDR_4: C76.2; also elsewhere on the board
/HDR_5: C77.2; also elsewhere on the board
/HDR_6: C78.2; also elsewhere on the board
/HDR_7: C79.2; also elsewhere on the board
/HDR_8: C104.2; also elsewhere on the board
/HDR_9: C105.2; also elsewhere on the board
/HDR_10: C106.2; also elsewhere on the board
/HDR_11: C107.2; also elsewhere on the board
/HDR_12: C132.2; also elsewhere on the board
/HDR_13: C133.2; also elsewhere on the board
/HDR_14: C134.2; also elsewhere on the board
/SPI0_RX: U9.7 (SDO), U12.7 (SDO), U15.7 (SDO); also elsewhere on the board
/SPI0_SCLK: U9.1 (SCLK), U12.1 (SCLK), U15.1 (SCLK); also elsewhere on the board
/SPI0_TX: U9.2 (SDIO), U12.2 (SDIO), U15.2 (SDIO); also elsewhere on the board
/~AMP_PD: U10.7 (PD2*), U10.15 (PD1*), U11.7 (PD2*), U11.15 (PD1*), U13.7 (PD2*), U13.15 (PD1*), U14.7 (PD2*), U14.15 (PD1*), U16.7 (PD2*), U16.15 (PD1*), U17.15 (PD1*); also elsewhere on the board
/~DDS2_CS: U9.8 (~CS); also elsewhere on the board
/~DDS3_CS: U12.8 (~CS); also elsewhere on the board
/~DDS4_CS: U15.8 (~CS); also elsewhere on the board
/~DDS_SYNC: U9.32 (~TRIGGER), U12.32 (~TRIGGER), U15.32 (~TRIGGER); also elsewhere on the board
/~EIT_PD: U17.7 (PD2*); also elsewhere on the board
/~RESET: U9.9 (~RESET), U12.9 (~RESET), U15.9 (~RESET); also elsewhere on the board
GND: C52.1, C53.1, C54.1, C56.2, C58.2, C59.1, C60.2, C61.2, C62.1, C63.1, C65.2, C67.2, C68.1, C69.2, C70.1, C71.2, C72.1, C73.2, C74.1, C75.2, C80.1, C81.1, C82.1, C84.2, C86.2, C87.1, C88.2, C89.2, C90.1, C91.1, C93.2, C95.2, C96.1, C97.2, C98.1, C99.2, C100.1, C101.2, C102.1, C103.2, C108.1, C109.1, C110.1, C112.2, C114.2, C115.1, C116.2, C117.2, C118.1, C119.1, C121.2, C123.2, C124.1, C125.2, C126.1, C127.2, C128.1, C129.2, C130.1, C131.2, R36.2, R38.2, R44.2, R46.2, R47.1, R48.1, R49.2, R50.1, R51.2, R61.2, R63.2, R69.2, R71.2, R72.1, R73.1, R74.2, R75.1, R76.2, R86.2, R88.2, R94.2, R96.2, R97.1, R98.1, R99.2, R100.1, R101.2, U9.3 (DGND), U9.15 (AGND), U9.19 (CLKGND), U9.26 (AGND), U9.33 (DGND), U10.17 (EP), U11.17 (EP), U12.3 (DGND), U12.15 (AGND), U12.19 (CLKGND), U12.26 (AGND), U12.33 (DGND), U13.17 (EP), U14.17 (EP), U15.3 (DGND), U15.15 (AGND), U15.19 (CLKGND), U15.26 (AGND), U15.33 (DGND), U16.17 (EP), U17.17 (EP); also elsewhere on the board
unnamed: C76.1, R52.1
unnamed: C77.1, R53.1
unnamed: C78.1, R54.1
unnamed: C79.1, R55.1
unnamed: C104.1, R77.1
unnamed: C105.1, R78.1
unnamed: C106.1, R79.1
unnamed: C107.1, R80.1
unnamed: C132.1, R102.1
unnamed: C133.1, R103.1
unnamed: C134.1, R104.1
unnamed: C135.1, R105.1
unnamed: C52.2, U9.22 (CLDO)
unnamed: C53.2, U9.6 (DLDO1)
unnamed: C54.2, U9.4 (DLDO2)
unnamed: R47.2, U9.24 (FSADJ2/CAL_SENSE), U9.25 (FSADJ1)
unnamed: C59.2, U9.18 (REFIO)
unnamed: R48.2, R52.2, U10.13 (OUT1)
unnamed: R49.1, R53.2, U10.5 (OUT2)
unnamed: R50.2, R54.2, U11.13 (OUT1)
unnamed: R51.1, R55.2, U11.5 (OUT2)
unnamed: C80.2, U12.22 (CLDO)
unnamed: C81.2, U12.6 (DLDO1)
unnamed: C82.2, U12.4 (DLDO2)
unnamed: R72.2, U12.24 (FSADJ2/CAL_SENSE), U12.25 (FSADJ1)
unnamed: C87.2, U12.18 (REFIO)
unnamed: R73.2, R77.2, U13.13 (OUT1)
unnamed: R74.1, R78.2, U13.5 (OUT2)
unnamed: R75.2, R79.2, U14.13 (OUT1)
unnamed: R76.1, R80.2, U14.5 (OUT2)
unnamed: C108.2, U15.22 (CLDO)
unnamed: C109.2, U15.6 (DLDO1)
unnamed: C110.2, U15.4 (DLDO2)
unnamed: R97.2, U15.24 (FSADJ2/CAL_SENSE), U15.25 (FSADJ1)
unnamed: C115.2, U15.18 (REFIO)
unnamed: R98.2, R102.2, U16.13 (OUT1)
unnamed: R99.1, R103.2, U16.5 (OUT2)
unnamed: R100.2, R104.2, U17.13 (OUT1)
unnamed: R101.1, R105.2, U17.5 (OUT2)
VCC: C69.1, C71.1, C73.1, C75.1, C97.1, C99.1, C101.1, C103.1, C125.1, C127.1, C129.1, C131.1, U10.6 (VS2+), U10.14 (VS1+), U11.6 (VS2+), U11.14 (VS1+), U13.6 (VS2+), U13.14 (VS1+), U14.6 (VS2+), U14.14 (VS1+), U16.6 (VS2+), U16.14 (VS1+), U17.6 (VS2+), U17.14 (VS1+); also elsewhere on the board
VSS: C68.2, C70.2, C72.2, C74.2, C96.2, C98.2, C100.2, C102.2, C124.2, C126.2, C128.2, C130.2, U10.4 (VS2-), U10.12 (VS1-), U11.4 (VS2-), U11.12 (VS1-), U13.4 (VS2-), U13.12 (VS1-), U14.4 (VS2-), U14.12 (VS1-), U16.4 (VS2-), U16.12 (VS1-), U17.4 (VS2-), U17.12 (VS1-); also elsewhere on the board

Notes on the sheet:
R_{SENSE} = 32 * V_{REFIO} / I_{OUTFS}
NC if using internal calibration resistors.

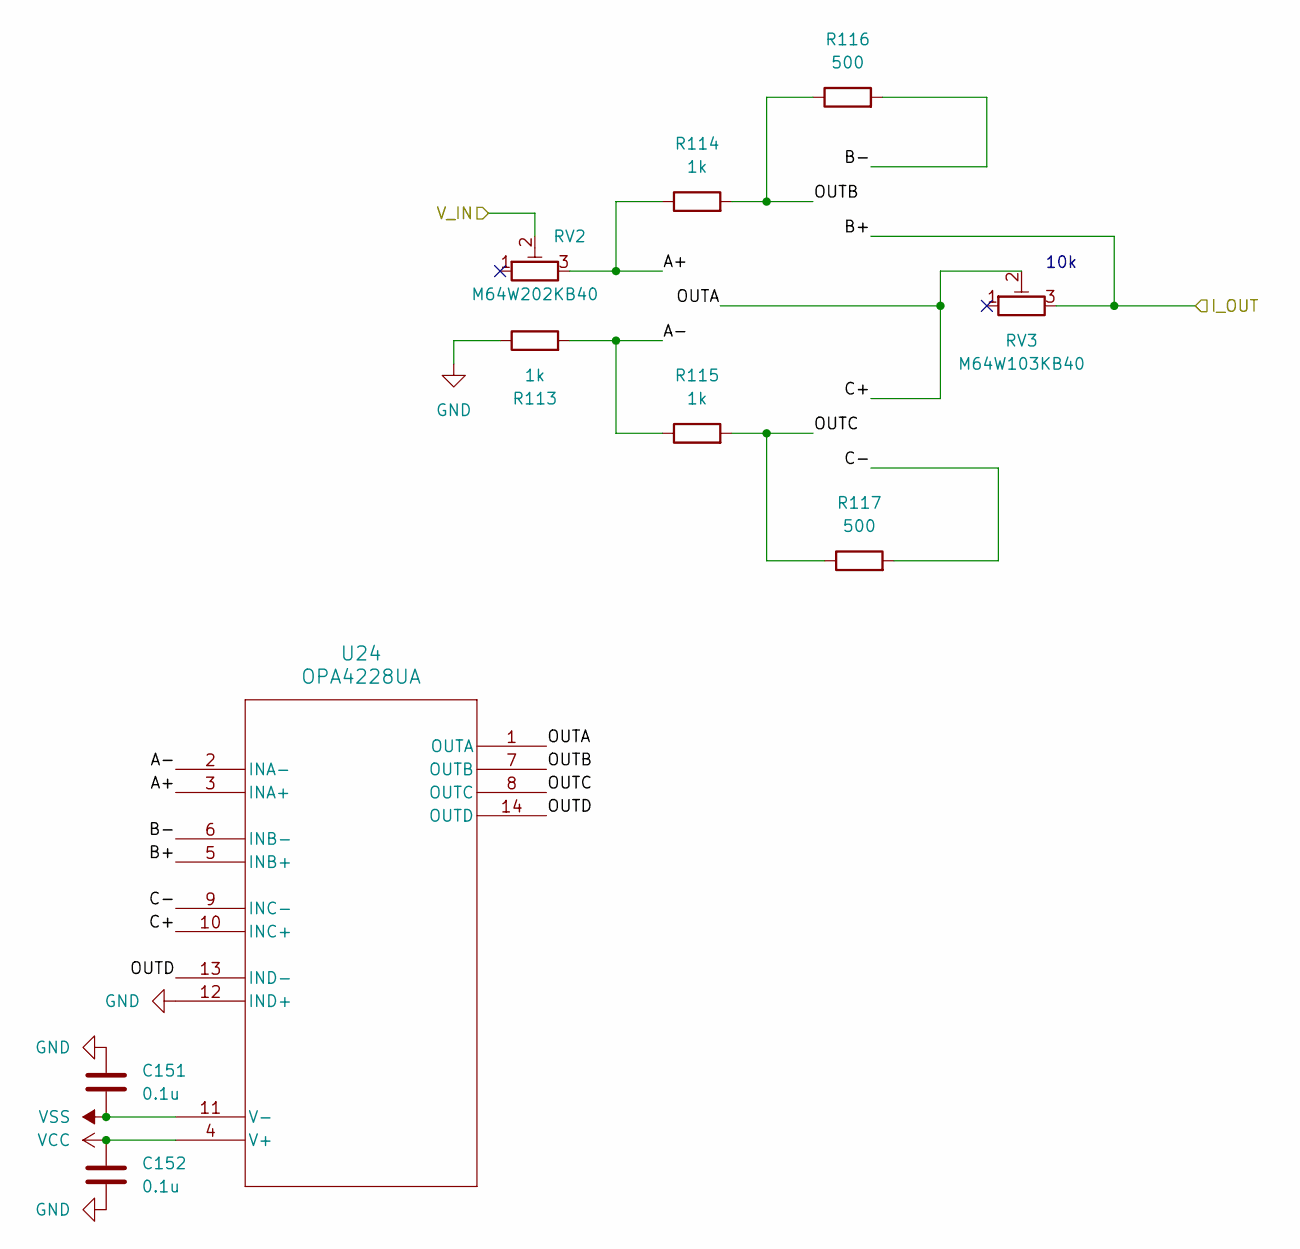
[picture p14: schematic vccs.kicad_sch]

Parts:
C151, C152: 0.1u; C_0603_1608Metric
R113, R114, R115: 1k; R_0603_1608Metric
R116, R117: 500; R_0603_1608Metric
RV2: M64W202KB40; POT_2023-08-01_VIS
RV3: M64W103KB40; POT_2023-08-01_VIS
U24: OPA4228UA; D14

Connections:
/Analog/CARRIER_SIG: RV2.2; also elsewhere on the board
/VCCS/A+: R114.1, RV2.3, U24.3 (INA+)
/VCCS/A-: R113.2, R115.1, U24.2 (INA-)
/VCCS/B-: R116.2, U24.6 (INB-)
/VCCS/C+: RV3.2, U24.1 (OUTA), U24.10 (INC+)
/VCCS/C-: R117.2, U24.9 (INC-)
/VCCS/OUTB: R114.2, R116.1, U24.7 (OUTB)
/VCCS/OUTC: R115.2, R117.1, U24.8 (OUTC)
/VCCS/OUTD: U24.13 (IND-), U24.14 (OUTD)
/VCCS_Iout: RV3.3, U24.5 (INB+); also elsewhere on the board
GND: C151.1, C152.2, R113.1, U24.12 (IND+); also elsewhere on the board
VCC: C152.1, U24.4 (V+); also elsewhere on the board
VSS: C151.2, U24.11 (V-); also elsewhere on the board

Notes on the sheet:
10k

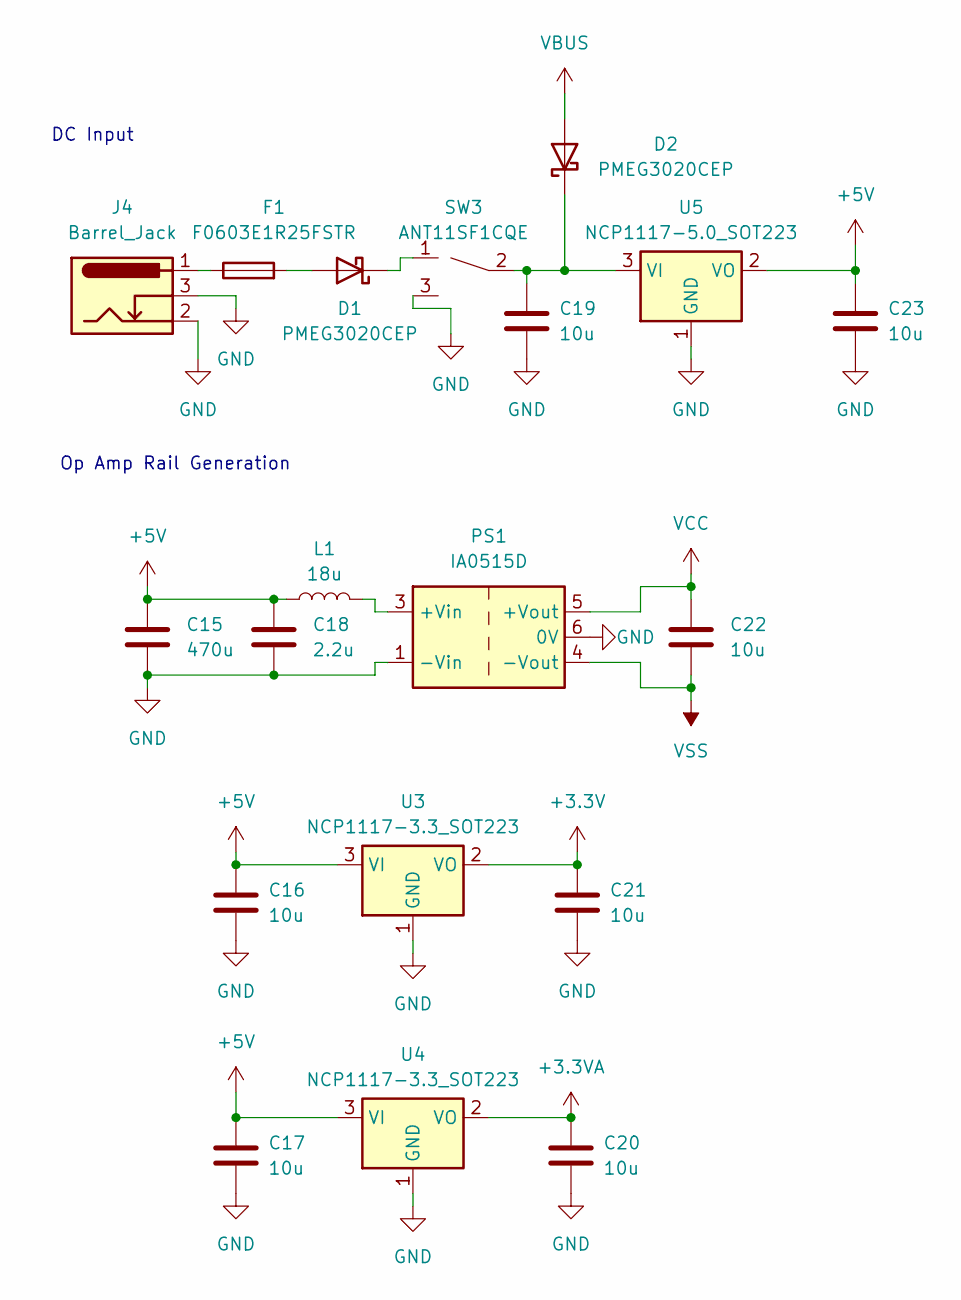
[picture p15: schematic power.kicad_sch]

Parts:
C15: 470u; CP_Radial_D6.3mm_P2.50mm
C16, C17, C19, C20, C21, C22, C23: 10u; C_0603_1608Metric
C18: 2.2u; C_0603_1608Metric
D1, D2: PMEG3020CEP; D_0603_1608Metric
F1: F0603E1R25FSTR; Fuse_0603_1608Metric
J4: Barrel_Jack; BarrelJack_GCT_DCJ200-10-A_Horizontal
L1: 18u; L_0603_1608Metric
PS1: IA0515D; Converter_DCDC_XP_POWER-IAxxxxD_THT
SW3: ANT11SF1CQE
U3, U4: NCP1117-3.3_SOT223; SOT-223-3_TabPin2
U5: NCP1117-5.0_SOT223; SOT-223-3_TabPin2

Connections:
+3.3V: C21.1, U3.2 (VO); also elsewhere on the board
+3.3VA: C20.1, U4.2 (VO); also elsewhere on the board
+5V: C15.1, C16.1, C17.1, C18.1, C23.1, L1.1, U3.3 (VI), U4.3 (VI), U5.2 (VO)
GND: C15.2, C16.2, C17.2, C18.2, C19.2, C20.2, C21.2, C23.2, J4.2, J4.3, PS1.1 (-Vin), PS1.6 (0V), SW3.3, U3.1 (GND), U4.1 (GND), U5.1 (GND); also elsewhere on the board
unnamed: D1.2 (A), F1.2
unnamed: D1.1 (K), SW3.1
unnamed: C19.1, D2.1 (K), SW3.2, U5.3 (VI)
unnamed: F1.1, J4.1
unnamed: L1.2, PS1.3 (+Vin)
VBUS: D2.2 (A); also elsewhere on the board
VCC: C22.1, PS1.5 (+Vout); also elsewhere on the board
VSS: C22.2, PS1.4 (-Vout); also elsewhere on the board

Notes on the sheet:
DC Input
Op Amp Rail Generation

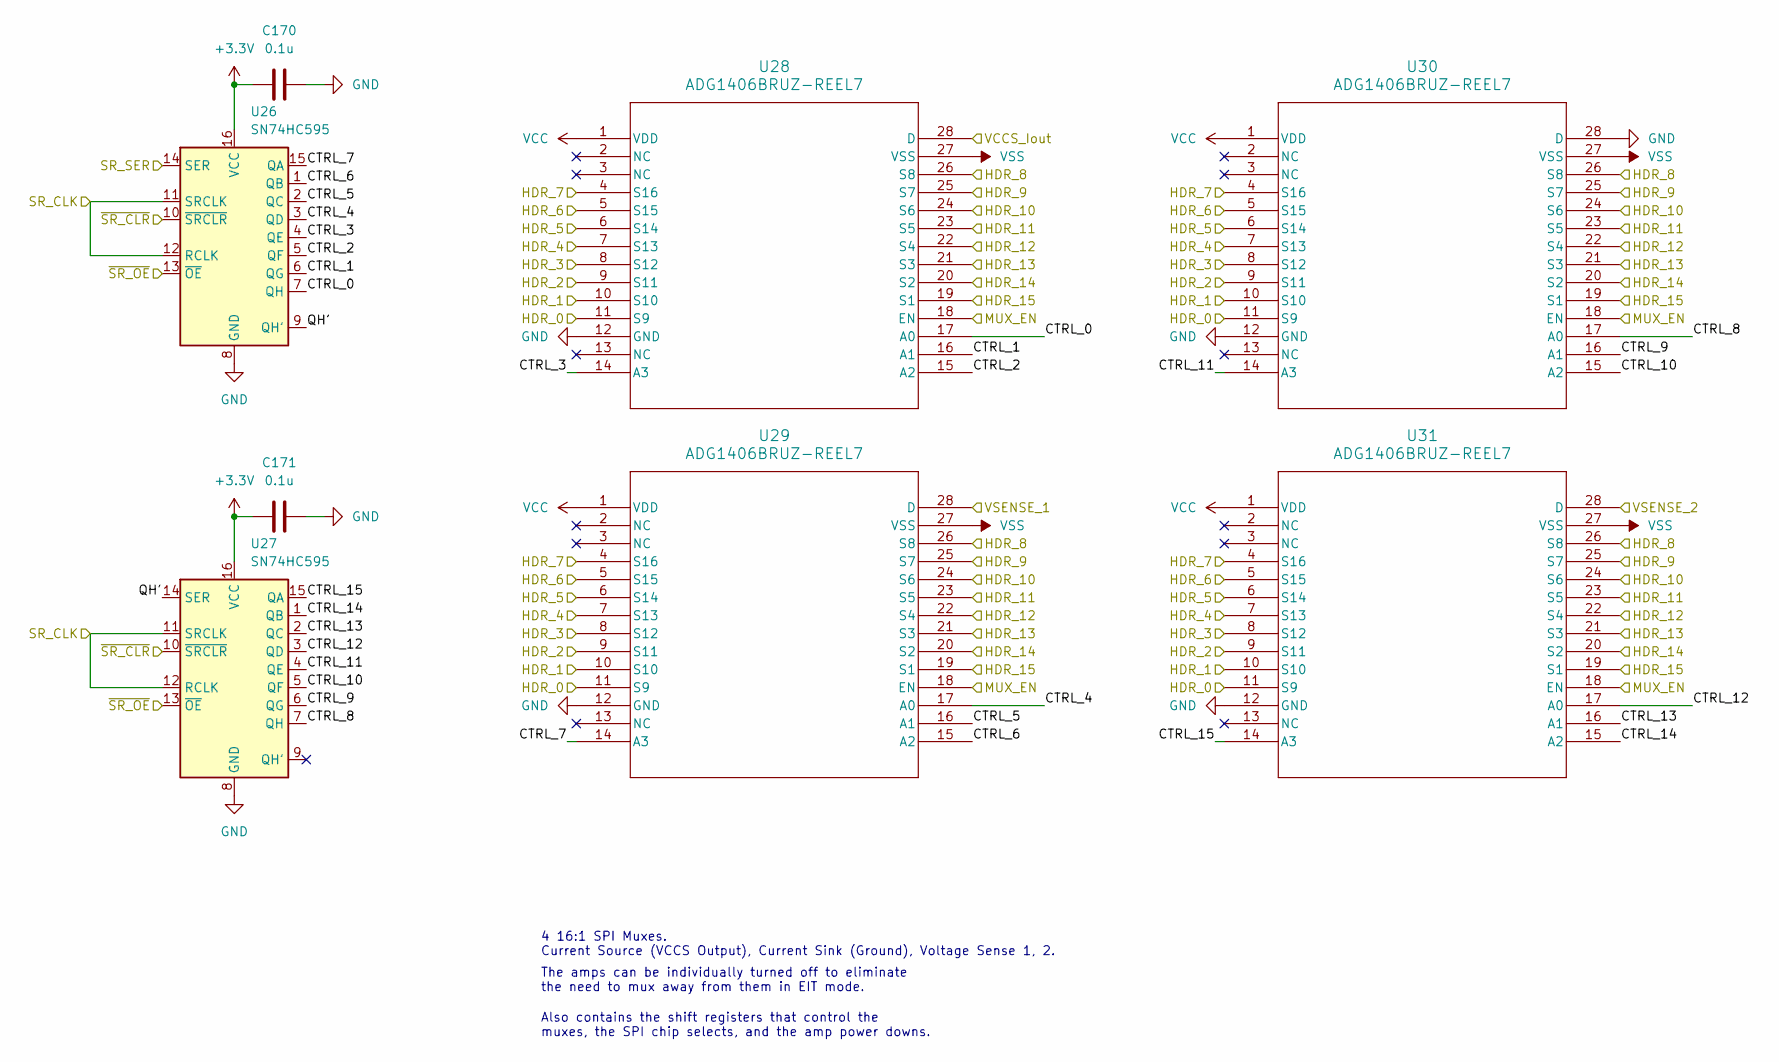
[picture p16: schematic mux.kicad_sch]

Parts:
C170, C171: 0.1u; C_0603_1608Metric
U26, U27: SN74HC595; SOIC-16W_5.3x10.2mm_P1.27mm
U28, U29, U30, U31: ADG1406BRUZ-REEL7; RU_28_ADI

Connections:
+3.3V: C170.1, C171.1, U26.16 (VCC), U27.16 (VCC); also elsewhere on the board
/Analog/SENSE_IN_1: U29.28 (D); also elsewhere on the board
/Analog/SENSE_IN_2: U31.28 (D); also elsewhere on the board
/HDR_0: U28.11 (S9), U29.11 (S9), U30.11 (S9), U31.11 (S9); also elsewhere on the board
/HDR_1: U28.10 (S10), U29.10 (S10), U30.10 (S10), U31.10 (S10); also elsewhere on the board
/HDR_2: U28.9 (S11), U29.9 (S11), U30.9 (S11), U31.9 (S11); also elsewhere on the board
/HDR_3: U28.8 (S12), U29.8 (S12), U30.8 (S12), U31.8 (S12); also elsewhere on the board
/HDR_4: U28.7 (S13), U29.7 (S13), U30.7 (S13), U31.7 (S13); also elsewhere on the board
/HDR_5: U28.6 (S14), U29.6 (S14), U30.6 (S14), U31.6 (S14); also elsewhere on the board
/HDR_6: U28.5 (S15), U29.5 (S15), U30.5 (S15), U31.5 (S15); also elsewhere on the board
/HDR_7: U28.4 (S16), U29.4 (S16), U30.4 (S16), U31.4 (S16); also elsewhere on the board
/HDR_8: U28.26 (S8), U29.26 (S8), U30.26 (S8), U31.26 (S8); also elsewhere on the board
/HDR_9: U28.25 (S7), U29.25 (S7), U30.25 (S7), U31.25 (S7); also elsewhere on the board
/HDR_10: U28.24 (S6), U29.24 (S6), U30.24 (S6), U31.24 (S6); also elsewhere on the board
/HDR_11: U28.23 (S5), U29.23 (S5), U30.23 (S5), U31.23 (S5); also elsewhere on the board
/HDR_12: U28.22 (S4), U29.22 (S4), U30.22 (S4), U31.22 (S4); also elsewhere on the board
/HDR_13: U28.21 (S3), U29.21 (S3), U30.21 (S3), U31.21 (S3); also elsewhere on the board
/HDR_14: U28.20 (S2), U29.20 (S2), U30.20 (S2), U31.20 (S2); also elsewhere on the board
/HDR_15: U28.19 (S1), U29.19 (S1), U30.19 (S1), U31.19 (S1); also elsewhere on the board
/MUX_EN: U28.18 (EN), U29.18 (EN), U30.18 (EN), U31.18 (EN); also elsewhere on the board
/Mux Control/CTRL_0: U26.7 (QH), U28.17 (A0)
/Mux Control/CTRL_1: U26.6 (QG), U28.16 (A1)
/Mux Control/CTRL_2: U26.5 (QF), U28.15 (A2)
/Mux Control/CTRL_3: U26.4 (QE), U28.14 (A3)
/Mux Control/CTRL_4: U26.3 (QD), U29.17 (A0)
/Mux Control/CTRL_5: U26.2 (QC), U29.16 (A1)
/Mux Control/CTRL_6: U26.1 (QB), U29.15 (A2)
/Mux Control/CTRL_7: U26.15 (QA), U29.14 (A3)
/Mux Control/CTRL_8: U27.7 (QH), U30.17 (A0)
/Mux Control/CTRL_9: U27.6 (QG), U30.16 (A1)
/Mux Control/CTRL_10: U27.5 (QF), U30.15 (A2)
/Mux Control/CTRL_11: U27.4 (QE), U30.14 (A3)
/Mux Control/CTRL_12: U27.3 (QD), U31.17 (A0)
/Mux Control/CTRL_13: U27.2 (QC), U31.16 (A1)
/Mux Control/CTRL_14: U27.1 (QB), U31.15 (A2)
/Mux Control/CTRL_15: U27.15 (QA), U31.14 (A3)
/Mux Control/QH': U26.9 (QH'), U27.14 (SER)
/SR_CLK: U26.11 (SRCLK), U26.12 (RCLK), U27.11 (SRCLK), U27.12 (RCLK); also elsewhere on the board
/SR_SER: U26.14 (SER); also elsewhere on the board
/VCCS_Iout: U28.28 (D); also elsewhere on the board
/~SR_CLR: U26.10 (~SRCLR), U27.10 (~SRCLR); also elsewhere on the board
/~SR_OE: U26.13 (~OE), U27.13 (~OE); also elsewhere on the board
GND: C170.2, C171.2, U26.8 (GND), U27.8 (GND), U28.12 (GND), U29.12 (GND), U30.12 (GND), U30.28 (D), U31.12 (GND); also elsewhere on the board
VCC: U28.1 (VDD), U29.1 (VDD), U30.1 (VDD), U31.1 (VDD); also elsewhere on the board
VSS: U28.27 (VSS), U29.27 (VSS), U30.27 (VSS), U31.27 (VSS); also elsewhere on the board

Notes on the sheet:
4 16:1 SPI Muxes. Current Source (VCCS Output), Current Sink (Ground), Voltage Sense 1, 2.
Also contains the shift registers that control the muxes, the SPI chip selects, and the amp power downs.
The amps can be individually turned off to eliminate the need to mux away from them in EIT mode.

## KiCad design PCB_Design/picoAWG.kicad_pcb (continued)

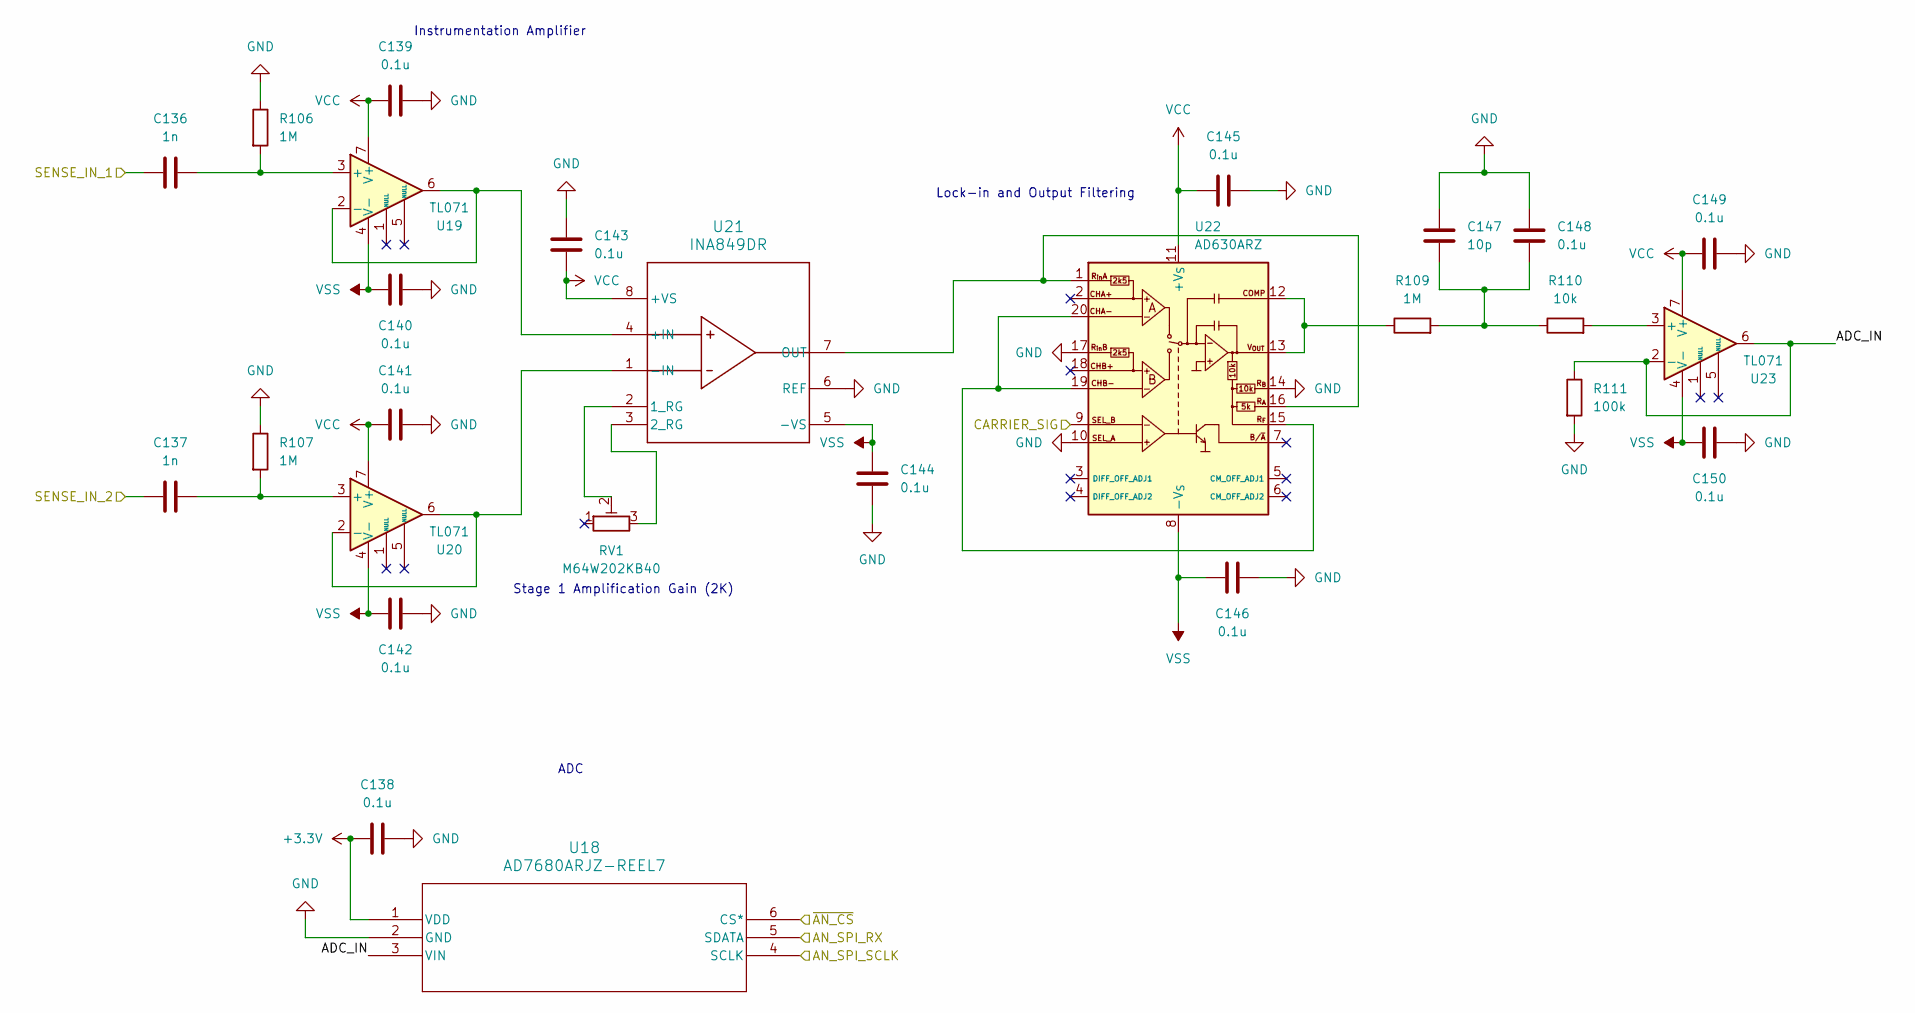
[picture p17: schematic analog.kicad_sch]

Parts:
C136, C137: 1n; C_0603_1608Metric
C138, C139, C140, C141, C142, C143, C144, C145, C146, C148, C149, C150: 0.1u; C_0603_1608Metric
C147: 10p; C_0603_1608Metric
R106, R107, R109: 1M; R_0603_1608Metric
R110: 10k; R_0603_1608Metric
R111: 100k; R_0603_1608Metric
RV1: M64W202KB40; POT_2023-08-01_VIS
U18: AD7680ARJZ-REEL7; RJ_6_ADI
U19, U20, U23: TL071; TSSOP-8_3x3mm_P0.65mm
U21: INA849DR; D0008A-IPC_A
U22: AD630ARZ; SOIC-20W_7.5x12.8mm_P1.27mm

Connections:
+3.3V: C138.1, U18.1 (VDD); also elsewhere on the board
/Analog/ADC_IN: R111.1, U18.3 (VIN), U23.2 (-), U23.6
/Analog/CARRIER_SIG: U22.9 (SEL_B); also elsewhere on the board
/Analog/SENSE_IN_1: C136.2; also elsewhere on the board
/Analog/SENSE_IN_2: C137.2; also elsewhere on the board
/SPI0_RX: U18.5 (SDATA); also elsewhere on the board
/SPI0_SCLK: U18.4 (SCLK); also elsewhere on the board
/~AN_CS: U18.6 (CS*); also elsewhere on the board
GND: C138.2, C139.2, C140.1, C141.2, C142.1, C143.2, C144.2, C145.1, C146.1, C147.1, C148.1, C149.2, C150.1, R106.1, R107.1, R111.2, U18.2 (GND), U21.6 (REF), U22.10 (SEL_A), U22.14 (R_{B}), U22.17 (R_{in}B); also elsewhere on the board
unnamed: C147.2, C148.2, R109.2, R110.1
unnamed: C136.1, R106.2, U19.3 (+)
unnamed: U19.2 (-), U19.6, U21.4 (+IN)
unnamed: C137.1, R107.2, U20.3 (+)
unnamed: U20.2 (-), U20.6, U21.1 (-IN)
unnamed: RV1.2, U21.2 (1_RG)
unnamed: RV1.3, U21.3 (2_RG)
unnamed: U21.7 (OUT), U22.1 (R_{in}A), U22.16 (R_{A})
unnamed: U22.15 (R_{F}), U22.19 (CHB-), U22.20 (CHA-)
unnamed: R109.1, U22.12 (COMP), U22.13 (V_{OUT})
unnamed: R110.2, U23.3 (+)
VCC: C139.1, C141.1, C143.1, C145.2, C149.1, U19.7 (V+), U20.7 (V+), U21.8 (+VS), U22.11 (+V_{S}), U23.7 (V+); also elsewhere on the board
VSS: C140.2, C142.2, C144.1, C146.2, C150.2, U19.4 (V-), U20.4 (V-), U21.5 (-VS), U22.8 (-V_{S}), U23.4 (V-); also elsewhere on the board

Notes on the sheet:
Lock-in and Output Filtering
Instrumentation Amplifier
ADC
Stage 1 Amplification Gain (2K)

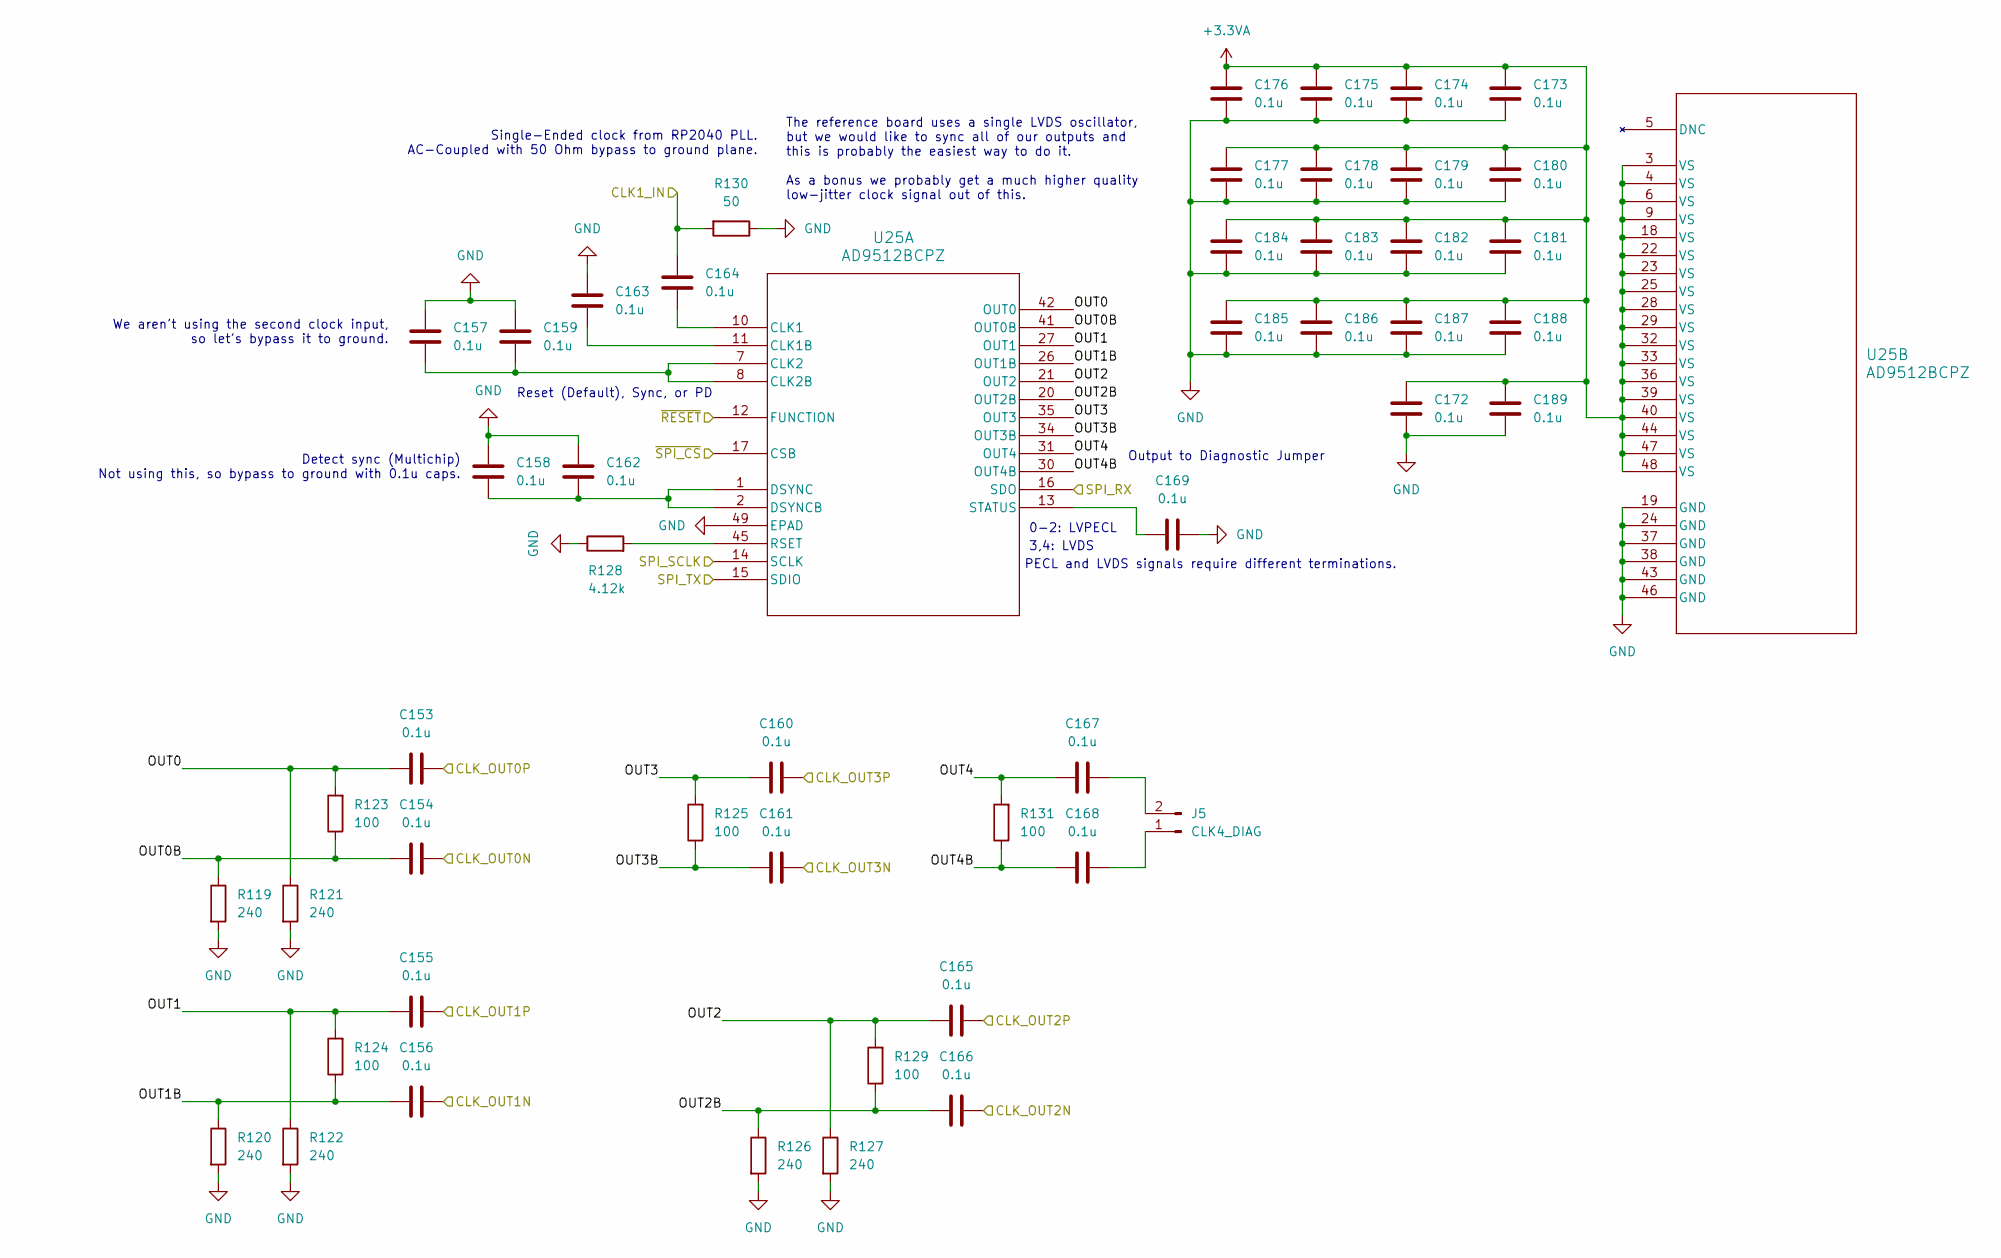
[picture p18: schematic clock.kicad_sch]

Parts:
C153, C154, C155, C156, C157, C158, C159, C160, C161, C162, C163, C164, C165, C166, C167, C168, C169, C172, C173, C174, C175, C176, C177, C178, C179, C180, C181, C182, C183, C184, C185, C186, C187, C188, C189: 0.1u; C_0603_1608Metric
J5: CLK4_DIAG; PinHeader_1x02_P2.54mm_Vertical
R119, R120, R121, R122, R126, R127: 240; R_0603_1608Metric
R123, R124, R125, R129, R131: 100; R_0603_1608Metric
R128: 4.12k; R_0603_1608Metric
R130: 50; R_0603_1608Metric
U25: AD9512BCPZ; CP_48_1_ADI

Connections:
+3.3VA: C172.1, C173.1, C174.1, C175.1, C176.1, C177.1, C178.1, C179.1, C180.1, C181.1, C182.1, C183.1, C184.1, C185.1, C186.1, C187.1, C188.1, C189.1, U25.3 (VS), U25.4 (VS), U25.6 (VS), U25.9 (VS), U25.18 (VS), U25.22 (VS), U25.23 (VS), U25.25 (VS), U25.28 (VS), U25.29 (VS), U25.32 (VS), U25.33 (VS), U25.36 (VS), U25.39 (VS), U25.40 (VS), U25.44 (VS), U25.47 (VS), U25.48 (VS); also elsewhere on the board
/CLK_0N: C154.2; also elsewhere on the board
/CLK_0P: C153.2; also elsewhere on the board
/CLK_1N: C156.2; also elsewhere on the board
/CLK_1P: C155.2; also elsewhere on the board
/CLK_2N: C166.2; also elsewhere on the board
/CLK_2P: C165.2; also elsewhere on the board
/CLK_3N: C161.2; also elsewhere on the board
/CLK_3P: C160.2; also elsewhere on the board
/Clock/OUT0: C153.1, R121.1, R123.2, U25.42 (OUT0)
/Clock/OUT0B: C154.1, R119.1, R123.1, U25.41 (OUT0B)
/Clock/OUT1: C155.1, R122.1, R124.2, U25.27 (OUT1)
/Clock/OUT1B: C156.1, R120.1, R124.1, U25.26 (OUT1B)
/Clock/OUT2: C165.1, R127.1, R129.2, U25.21 (OUT2)
/Clock/OUT2B: C166.1, R126.1, R129.1, U25.20 (OUT2B)
/Clock/OUT3: C160.1, R125.2, U25.35 (OUT3)
/Clock/OUT3B: C161.1, R125.1, U25.34 (OUT3B)
/Clock/OUT4: C167.1, R131.2, U25.31 (OUT4)
/Clock/OUT4B: C168.1, R131.1, U25.30 (OUT4B)
/SPI1_RX: U25.16 (SDO); also elsewhere on the board
/SPI1_SCLK: U25.14 (SCLK); also elsewhere on the board
/SPI1_TX: U25.15 (SDIO); also elsewhere on the board
/uC_CLKOUT: C164.1, R130.2; also elsewhere on the board
/~CLK_CS: U25.17 (CSB); also elsewhere on the board
/~RESET: U25.12 (FUNCTION); also elsewhere on the board
GND: C157.1, C158.2, C159.1, C162.2, C163.1, C169.1, C172.2, C173.2, C174.2, C175.2, C176.2, C177.2, C178.2, C179.2, C180.2, C181.2, C182.2, C183.2, C184.2, C185.2, C186.2, C187.2, C188.2, C189.2, R119.2, R120.2, R121.2, R122.2, R126.2, R127.2, R128.1, R130.1, U25.19 (GND), U25.24 (GND), U25.37 (GND), U25.38 (GND), U25.43 (GND), U25.46 (GND), U25.49 (EPAD); also elsewhere on the board
unnamed: C168.2, J5.1
unnamed: C167.2, J5.2
unnamed: C164.2, U25.10 (CLK1)
unnamed: C163.2, U25.11 (CLK1B)
unnamed: C157.2, C159.2, U25.7 (CLK2), U25.8 (CLK2B)
unnamed: C158.1, C162.1, U25.1 (DSYNC), U25.2 (DSYNCB)
unnamed: R128.2, U25.45 (RSET)
unnamed: C169.2, U25.13 (STATUS)

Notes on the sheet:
The reference board uses a single LVDS oscillator, but we would like to sync all of our outputs and this is probably the easiest way to do it. As a bonus we probably get a much higher quality low-jitter clock signal out of this.
PECL and LVDS signals require different terminations.
0-2: LVPECL
We aren't using the second clock input, so let's bypass it to ground.
Reset (Default), Sync, or PD
3,4: LVDS
Output to Diagnostic Jumper
Detect sync (Multichip) Not using this, so bypass to ground with 0.1u caps.
Single-Ended clock from RP2040 PLL. AC-Coupled with 50 Ohm bypass to ground plane.

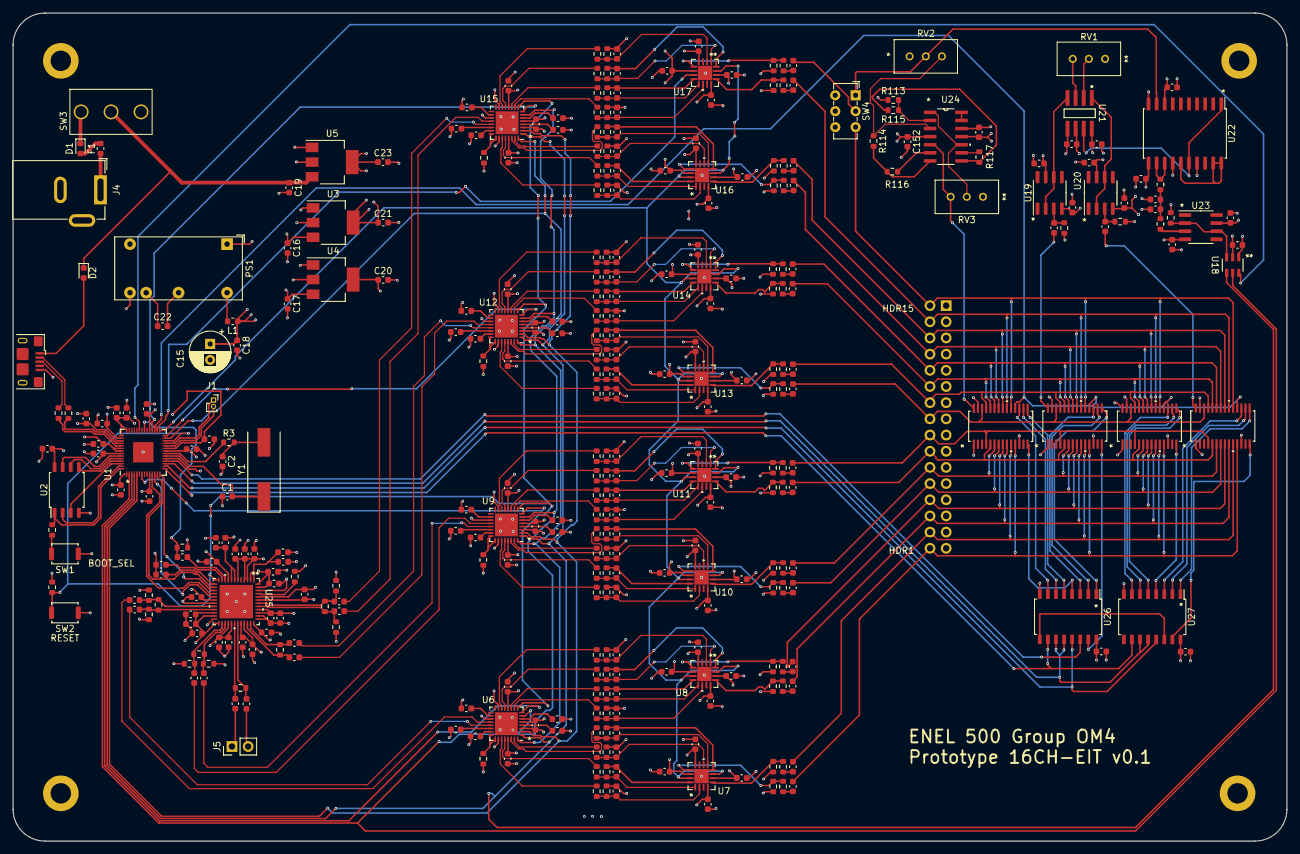
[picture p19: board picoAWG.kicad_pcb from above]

Board: 4 copper layers, 200.0 x 130.0 mm, 366 parts (1 on the bottom side), 267 nets.

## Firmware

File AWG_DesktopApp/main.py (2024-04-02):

import PySimpleGUI as sg
import math
import string
import numpy as np
import matplotlib
import matplotlib.pyplot as plt
from   matplotlib.backends.backend_tkagg import FigureCanvasTkAgg
#do pip install pyserial, pyusb and pytime
import serial.tools.list_ports
import time

import wavegen
import user_serial

# Global Variables
mode=0
channel_count = 16
current_channel = 0
graph_size_x=900
graph_size_y=375
use_custom_titlebar = False
channel_list = ["Channel " + str(i) for i in range(0,15,1)]

# Variables for keeping track of channel parameters and status
# Initialize to default values
channel_frequencies = [15.0]*channel_count #In kHz
channel_amplitude = [1.0]*channel_count
channel_phase = [0.0]*channel_count
channel_wavetype = ['Sine']*channel_count
channel_status = [False]*channel_count

# make_window()
# This function defines the layouts, then draws the window
# returns the window to be drawn
def make_window(mode,theme=None):

    NAME_SIZE = 16

    #font to use
    interface_font='Courier 10'

    # name(name)
    # Creates a pySimpleGUI Text element and populates it with given text
    # takes in a string value to add to the text element
    def name(name):
        return sg.Text(name + ' ' + ':', size=(NAME_SIZE,1), justification='left',pad=(0,0), font=interface_font)

    sg.theme(theme)

    # Layouts
    ##### Standard Waveform Generator Layout
    # This is the left side layout that includes the statuses of all the channels
    layout_l = [[ sg.Text('Status',font='Courier 16')],
                [ sg.HSep()],
                *[[sg.Col([[sg.Text(f'Channel {i}'),sg.Text('●', size=(1, 1), text_color='red',key=f'-CIRCLE{i}-')]]) ]for i in range(0,channel_count)],
                ]

    #  Right side layout
    parameter_layout =[[name('Frequency(kHz)'), sg.Spin([round(i * 0.1, 1) for i in range(150, 5000)],initial_value=15.0, s=(15,2), k='-FREQUENCY-', enable_events=True)],
                       [name('Amplitude(V)'), sg.Spin([round(i * 0.1, 1) for i in range(0, 150)],initial_value=1.0, s=(15,2), k='-AMPLITUDE-'),sg.Button('Set',expand_x=True, enable_events=True, k='-SETPARAMS-')],
                       [name('Phase Shift(°)'), sg.Spin([round(i * 0.1, 1) for i in range(-3600, 3600)],initial_value=0.0, s=(15,2),k='-PHASE-')],
                       #[name('Offset'), sg.Spin(['0 V',], s=(15,2))]
                       ]
    # Layout that contains the presets for the waves
    preset_layout =[[name('Preset waves'), sg.Combo(['Sine', 'Cosine', 'Square', 'Saw Up', 'Saw Down', 'Triangle'], default_value='Sine', s=(15,22), enable_events=False, readonly=True, k='-PRESET-')],
                       [sg.Button('Use',expand_x=True, enable_events=True, k='-SETPRESET-')],
                       ]

    ## Layout for determining the Input/Output and Mode of the AWG
    ### Currently unused, may be re-added in the future
    function_layout =[[name('Input/Output:'), sg.Combo(['Output','Input'], default_value='Output', s=(15,22), enable_events=False, readonly=True, k='-FUNCTION-')],
                      [name('Mode:'), sg.Combo(['DAC','ADC'], default_value='Output', s=(15,22), enable_events=False, readonly=True, k='-MODE-')]
                       ]
    ## The layout that includes the ON/OFF slider button
    button_layout =[[sg.Slider(range=(0, 1), default_value=0, orientation='h', size=(8, 40), key='-SLIDER-', enable_events=True,tooltip='Toggle On/Off',disable_number_display=True),

                        ],
                        [sg.Text('State: '), sg.Text('Off', size=(5,1), key='-STATE-'),]
                ]

    ## This is the layout for the parameter and channel control; Includes Parameter layout, preset layout and On/Off layout
    # frame_layout = [[sg.Graph((graph_size_x+80, graph_size_y+20), (0,20), (graph_size_x,graph_size_y),background_color='white', k='-GRAPH-')],
    frame_layout = [[sg.Canvas(size=(graph_size_x+80, graph_size_y+20), k='-AWG-GRAPH-')],
                    [
                       sg.Column([[sg.Frame("Parameters",parameter_layout)]]),
                       sg.Column([[sg.Frame("Presets",preset_layout)]]),
                     #  sg.Column([[sg.Frame("Function",function_layout,expand_y=True)]]),
                       sg.Column([[sg.Frame("On/Off",button_layout,expand_y=True)]])
                    ]
                 ]
    ## Layout for the right side of the Interface; Includes the Graph, Channel name and all the parameter controls
    layout_r  = [[sg.Text("Channel " + str(current_channel), k='-CHANNELTEXT-'),sg.Push(),sg.Combo(channel_list, default_value="Channel " + str(current_channel), size=(15,22), enable_events=True, readonly=True, k='-CHANNELNUM-',)],
                 [sg.Frame("Waveform",frame_layout)]]
    #############################################
    ### EIT Layout ###
    layout_eit_parameters = [[sg.Push(),sg.Text('Electrodes :',font=interface_font), sg.Spin(['0',], s=(15,2), k='-ELECTRODES-')],
                       [sg.Push(),sg.Text('Distance Between Electrodes (m) :',font=interface_font), sg.Spin(['0',], s=(15,2), k='-ELECTRODESD-')],
                       #[sg.Push(),sg.Text('Amplitude (V) :',font=interface_font), sg.Spin(['0',], s=(15,2),k='-AMPLITUDE2-')],
                       [sg.Push(),sg.Text('Frequency of Injected Current (Hz) :',font=interface_font), sg.Spin(['0',], s=(15,2),k='-FREQUENCY2-')],
                       #[sg.Push(),sg.Text('Voltage Out (V) :',font=interface_font), sg.Spin(['0',], s=(15,2),k='-VOLTAGEOUT-')],
                       [sg.Button('Submit',expand_x=True, enable_events=True, k='-SUBMITEIT-')],
                       [sg.Checkbox('Enable EIT', k='-EIT_EN-')]
                       ]
    layout_eit = [
                    [
                        sg.Column([
                            [sg.Text('Electrical Impedance Tomography (EIT)',font='Courier 16')],
                            [sg.Column([[sg.Frame("Parameters",layout_eit_parameters)]])],
                            [sg.Canvas(size=(450,450), k='-EIT-GRAPH-')]
                            # [sg.Frame("",[[sg.Graph((450,450),(0,450),(450,0),background_color='white',border_width=1)]])]
                        ],element_justification='center')
                    ]
                  ]

    ###################

    ### Window drawing ###
    layout = [ [sg.Col(layout_l,size=(None,None),expand_x=True, expand_y=True, pad=(0,0), ), sg.VSep(), sg.Col(layout_r,vertical_alignment='top')]]

    eit_window_layout = [[ sg.Col(layout_eit,vertical_alignment='top')]]


    main_layout = [
        [
            sg.Menu([['File', ['Import', 'Export', 'Exit']], ['Tools', ['EIT']], ['Help', ['User Manual', 'Basics']]],
                    k='-CUST MENUBAR-', p=0)
        ],
        [
            sg.Column(
                [
                    [
                        sg.Column(eit_window_layout, visible=(mode == "eit"), key='-EIT-'),
                        sg.Column(layout, visible=(mode == "awg"), key='-AWG-')
                    ]
                ],
                key='-MAIN COLUMN-', justification= 'center'
            )
        ]
    ]
    window_size= (1080,700)

    window = sg.Window('16 Channel Arbitrary Waveform Generator', main_layout, finalize=True,  keep_on_top=False, use_custom_titlebar=use_custom_titlebar, size= window_size)


    return window

def to_int (str:str):
    return int(str.strip(string.ascii_letters + string.punctuation))

def get_bool (array,index):
    string = array[index]
    if string == "On":
        return True
    if string == "Off":
        return False

def gen_graph_data (ch_n):
    return wavegen.gen_graph(channel_frequencies[ch_n] * 1000, # Converting to kHz
                             channel_phase[ch_n],
                             channel_wavetype[ch_n]) # "SINE")

def update_graph (ch_n:int, ax:plt.axes, canvas):
    ax.clear()
    x, y = gen_graph_data (ch_n)
    user_serial.awg_update(y, current_channel)
    # Do a graph update
    ax.plot(x,y)
    canvas.draw()
    canvas.get_tk_widget().pack(side='top', fill='both', expand=1)
    pass

# change_channel(window)
# This function handles all events for when a channel is changes
# Includes saving the current parameters and calling the function for sending a serial message
# and then retrieving the parameters for the channel that was switched to.
# takes in the window to access the elements
def change_channel(window):
    # The current parameters are already saved by the parameter update event. There's no need to do that here.
    #Update the window with the new channel parameters
    channel_disp = values['-CHANNELNUM-'] # Get the updated channel number (Starting at 1)
    # window['-CHANNELTEXT-'].update(channel_disp)
    global current_channel
    current_channel = to_int(channel_disp)

    # Retrieve the values associated with the new channel
    amplitude_input = channel_amplitude[current_channel]
    frequency_input = channel_frequencies [current_channel]
    phase_input = channel_phase [current_channel]
    use_preset = channel_wavetype[current_channel]

    # Reflect those new values in the GUI
    window['-FREQUENCY-'].update(frequency_input)
    window['-AMPLITUDE-'].update(amplitude_input)
    window['-PHASE-'].update(phase_input)
    window['-PRESET-'].update(use_preset)

    if channel_status[current_channel] == False:
        window['-SLIDER-'].update(value=0)
        window['-STATE-'].update('Off')
    else:
        window['-SLIDER-'].update(value=1)
        window['-STATE-'].update('On')

    update_graph(current_channel, ax_awg, awg_canvas_agg)

#check_params(amplitude, frequency, phase)
#checks if the parameters are within the expected ranges
# If the input is invalid, create a popup
# Returns a boolean: True if the input is valid, False otherwise
def check_params(amplitude, frequency, phase):
    message = "ERROR: \n"
    invalid_input = False
    if ((amplitude < 0) or (amplitude > 15)):
        message += "Amplitude input is invalid. Must be between 0 V and 15 V.\n"
        invalid_input = True
    if (frequency < 15) or (frequency > 500):
        message += "Frequency input is invalid. Must be between 15 kHz and 500 kHz.\n"
        invalid_input = True
    if (phase < -360) or (phase > 360):
        message += "Phase input is invalid. Must be between -360° and 360° \n"
        invalid_input = True

    if invalid_input == True:
        sg.popup_error(message, title="Error: Invalid Input")
        return False
    else:
        return True

# change_params(amplitude, frequency, phase)
# This handles the modification of the Parameters being sent to the RP2040
# Calls the check_params function to make sure the input is valid
# Takes in the amplitude, frequency and phase as floats.
def change_params(amplitude, frequency, phase):
    valid_input = check_params(amplitude, frequency, phase)
    if valid_input == True:
        print("Parameters sent: ", amplitude,frequency, phase)
        # send_serial_message(str("Params of "+str(amplitude)+","+str(frequency)+","+str(phase)+"\n"))

# Start of the program...

window = make_window("awg")

# Create new graph based on the current data on the channel

# Attach new graph to the AWG-GRAPH and EIT-GRAPH keys.
fig_awg, ax_awg = plt.subplots()
fig_awg.set_dpi(100)
fig_awg.set_size_inches(9, 3.75)
awg_canvas_agg = FigureCanvasTkAgg(fig_awg, window['-AWG-GRAPH-'].TKCanvas)
update_graph(current_channel, ax_awg, awg_canvas_agg)

fig_eit, ax_eit = plt.subplots()
fig_eit.set_dpi(100)
fig_eit.set_size_inches(4.5, 4.5)
eit_canvas_agg = FigureCanvasTkAgg(fig_eit, window['-EIT-GRAPH-'].TKCanvas)
ax_eit.plot()
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

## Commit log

2023-03-31 PCB Design Added
2023-04-05 Added Enclosure Design
    [AWG v1.f3d, AWG v1_Bottom.stl, AWG v1_Top.stl, BoardOutline.dxf]
2024-01-09 Change PCB to KiCAD
    Basic project framework. PCB design coming in future commits
    [picoAWG.kicad_pcb, picoAWG.kicad_sch]
2024-02-09 Schematic v1
    [analog.kicad_sch, clock.kicad_sch, dds.kicad_sch, mux.kicad_sch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]
2024-02-10 Added Mesh View Button To GUI
    [mesha06_bumpychestslice_radiological_view_both_lungs_1_0-3.ply]
2024-03-01 KiCAD file update, completed PCB
    [analog.kicad_sch, bom.csv, dds.kicad_sch, designators.csv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]
2024-03-03 Slight board updates - Added board PDFs and images
    [dds.kicad_sch, picoAWG.kicad_pcb, power.kicad_sch]
2024-03-05 Final KiCAD Files Submitted to JLC PCB
    [BOM-picoAWG.csv, CPL-picoAWG.csv, bom.csv, designators.csv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]
2024-03-15 Updated Meshes
    [Circle.ply, mesha06_bumpychestslice_radiological_view_both_lungs_1_0-3.ply]
2024-03-20 Update KiCAD files to KiCAD 8.0
    [analog.kicad_sch, clock.kicad_sch, dds.kicad_sch, mux.kicad_sch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]
2024-03-20 Updated PCB Board Images
2024-03-26 PCB Gitignore and PDF
2024-03-29 [03/28/2024] Removed Voltages from EIT Interface, Made Changes to AWG interface
    AWG:
    - Fixed ranges for the spin elements for the parameters
    -Re-added mode, mistake of deleting it earlier
    - Reorganized some of the code to have the global variables at the top
